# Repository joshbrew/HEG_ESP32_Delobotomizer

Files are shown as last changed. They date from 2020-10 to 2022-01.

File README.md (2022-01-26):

# HEG ESP32 - Delobotomizer Edition

Official repository for the HEGduino V2 Delobotomizer firmware, software, and designs.

### [WebApp: Brains@Play](https://app.brainsatplay.com)
- This will replace the original software and is MUCH more robust, we are still doing a lot of legwork to get all of the quality of life features we want into it but welcome to the new multi-bci community framework for the web! 
- Chrome only for desktop, works on Android and in VR. 
- Find the install button via the settings button in the top right of the browser.
### [Getting Started (click me)](https://github.com/moothyknight/HEG_ESP32_Delobotomizer/blob/main/Guides/GettingStarted.md)
### [Updating Your Device](https://github.com/moothyknight/HEG_ESP32_Delobotomizer/blob/main/Guides/Updating.md)
### [Whitepaper](https://github.com/moothyknight/HEG_ESP32_Delobotomizer/blob/main/Guides/Open%20Source%20HEG_FNIRS%20Whitepaper.pdf)
### [Old Progressive Web App (no longer updated)](https://hegalomania.netlify.app) 
- Original webapp demo, use via Chrome for Serial USB support. Use BLE mode if the USB device is not recognized in browser, this is a known issue. If that fails use the web server with the device in WiFi mode.

### If your browser won't identify the USB connection, try installing the VCP for Windows (or Mac) drivers here: https://www.silabs.com/developers/usb-to-uart-bridge-vcp-drivers

## Firmware

The Firmware folder contains a .bin file that you can use via the on-board web interface to update the device. There are Arduino libraries and firmware code files for custom code, you will need the ESP32 module additionally for Arduino.

Simply connect to the wifi network named "My_HEG" when the device is powered up with password "12345678"

In your preferred browser, enter "192.168.4.1" into the address bar. You should see an interface show up. Click on the Update button to go to the update page.

Now follow the instructions on screen to browse for the .bin folder that you may download from this repo. Wait for it to finish uploading then reconnect to the HEG after that's taken care of if it does not do it automatically. Voila!

## Progressive Web App (WIP): https://hegalomania.netlify.app

Our new preferred method for using the HEG, a state of the art Progressive Web App! 

Open this link to use your HEG in a Chrome browser or Android for instant access to using your device. This is being updated to a React app with a more familiar UI and a more concise code base to expand from.

You may install it locally on desktop or mobile as well just like any app and create desktop shortcuts. For desktop open the settings bar in Chrome and click "Install HEG Alpha." The USB mode only works in chrome right now as it is a development feature. You can enable this feature by going to chrome://flags and enabling the "Experimental Web Platform features" flag. For mobile it should prompt you to install, if not find the install button in your chrome settings menu on mobile.

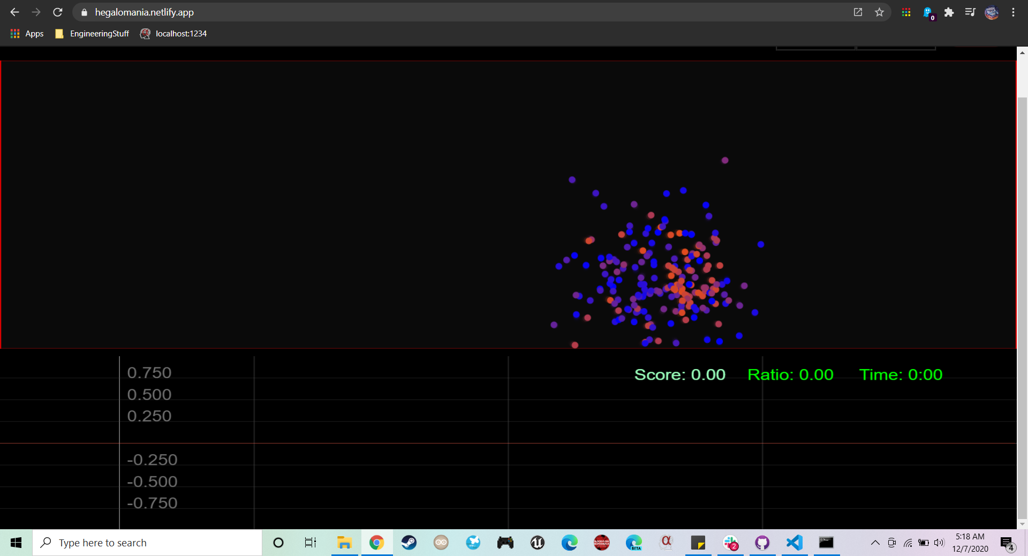
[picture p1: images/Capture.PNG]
Boids


## Boot routine

The newer firmware contains a new boot-up routine for making it easier to identify streaming modes on the device. It will flash when powered up to indicate which mode it's in.

On boot:
* Two fast blinks: BLE mode
* Three fast blinks: WIFI mode
* Four fast blinks: Bluetooth Classic (Serial) mode

The button on the newer devices puts your device to sleep. There will be a switch added next to control device settings.

Since your device is covered in tape this will help you find the reset button if I didn't mark it for you:
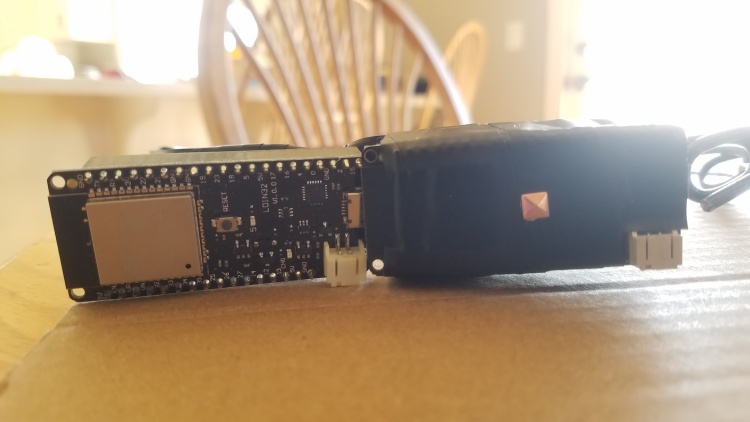
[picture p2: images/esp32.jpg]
esp32


## Device Commands (accessible via app (Send Command button) or serial monitor)

* 't' - Turn sensor ON (automatic)
* 'f' - Turn sensor OFF, device will go to sleep after 10min of inactivity
* 'b' - BLE mode toggle. Toggles back to WiFi mode.
* 'B' - Bluetooth Serial toggle. Toggles back to WiFi mode.
* 'W' - Reset WiFi credentials (if it won't connect to your router)
* 'R' - Reboot device
* 'S' - Enter deep sleep mode e.g. to save battery
* 'u' - USB only output mode (no wireless signals)
* 'o' - Fast output mode (<20 byte packets for Android Web BLE)
* 'L' - External LED mode, configured for pins 12 and 14 to run LEDs and be sampled.
* 'N' - Toggle SPO2 output (experimental, not working properly yet)
* 'D' - Toggle Debug output (for using Arduino's graphing)
* 'e' - Toggle exposure settings: slow, fast, and default. default has the slowest output rate but samples faster than slow mode with more averaging.
* 'l' - Toggle LED protocols in this order: Ambient,IR,2 IR (AMBIENT, LED2, LED1+2); Red,IR,2 IR (LED3, LED2, LED1+2), Red = IR (LED1, LED2, AMB), or Default (LED3,LED2,AMBIENT)
* 'X' - DC filter toggle
* 'F' - Digital filter toggle
Note, use the first setting with the command 'l' if your red LED is underperforming. This will make the software compare Ambient and IR, and optional both IR LEDs for extra strength. For some reason the red output is not as consistent for some people.

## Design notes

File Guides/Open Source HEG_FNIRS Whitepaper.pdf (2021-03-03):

Joshua Brewster
October 2020

## Open Source, Low Cost, Scalable fNIRS/HEG Whitepaper

Contents

Abstract | 2
Acronyms | 2
FNIRS Overview | 3
HEG Biofeedback Overview | 9
List of HEG Case Studies | 17
HEG Alpha | 18
Citations from Hyperlinks | 24

Abstract:
This whitepaper is to cover what I’ve learned from functional Near Infrared Spectroscopy (fNIRS) and Hemoencephalography (HEG) biofeedback as well as my development progress on open source low cost tools for anyone to jump into this space and benefit from it either for education or home therapy. These are important emerging imaging and therapeutic technologies as they offer a low cost and low abstraction method to work with live or recorded information from the brain. This is paired with a type of brain blood flow training for biofeedback therapy that allows users to increase their baseline brain perfusion in their prefrontal cortex and beyond. This field promises even more interesting monitoring methods and psychiatric tools akin to functional Magnetic Resonance Imaging (fMRI) with the use of tomography (DOT), laser interferometry (OCT), and deep learning feature decoders to understand brain activity. Our goal is to carve a path for open source efforts in this area by developing low cost tools and free software through reproducing different public domain hardware and experiments. We are sharing working and tested plans free, and hardware low cost.

Acronyms:
fNIRS - Functional Near Infrared Spectroscopy HEG - Hemoencephalography
EEG - Electroencephalography
HbO2 - Oxygenated Hemoglobin
Hb - Deoxygenated Hemoglobin SpO2 - Pulsatile Oxygen Saturation
CBF - Cerebral Blood Flow
DOT - Diffuse Optical Tomography
fMRI - Functional Magnetic Resonance Imaging OCT - Optical Coherence Tomography

fNIRS overview:

Here will give a brief overview of the essential concepts of Functional Near Infrared Spectroscopy (fNIRS) and brain blood flow biofeedback. The Hemoencephalography (HEG) device is simply a single sensor fNIRS device with red and infrared wavelengths standard to pulse oximetry, and 3 cm spacing for depth readings. Alternatively it has been done with thermocouples to just measure IR radiation off your forehead, while photodiodes also include optical wavelengths. You can view the original patent 5995857 by Hershel Toomim and Bob Marsh, now public domain, online. (https://patents.google.com/patent/US5995857A/en)

fNIRS is the application of near infrared light, and more generally optical wavelengths, for the purpose of imaging the surface of the brain and monitoring Cerebral Blood Flow (CBF). It is much cheaper but not as complete as a functional Magnetic Resonance Imaging (fMRI) scan with tracer injections, though it can still elucidate a ton of useful structural and functional data about the brain. The skull is highly translucent and even lends itself well for optical imaging of the brain. This is accomplished by placing LED or laser emitters with specific wavelengths at specific distances from photosensors on the scalp or forehead and flashing them repeatedly while reading the response on the photodiode. Your pulse for example is plainly visible by this method and blood oxygen can be calculated.

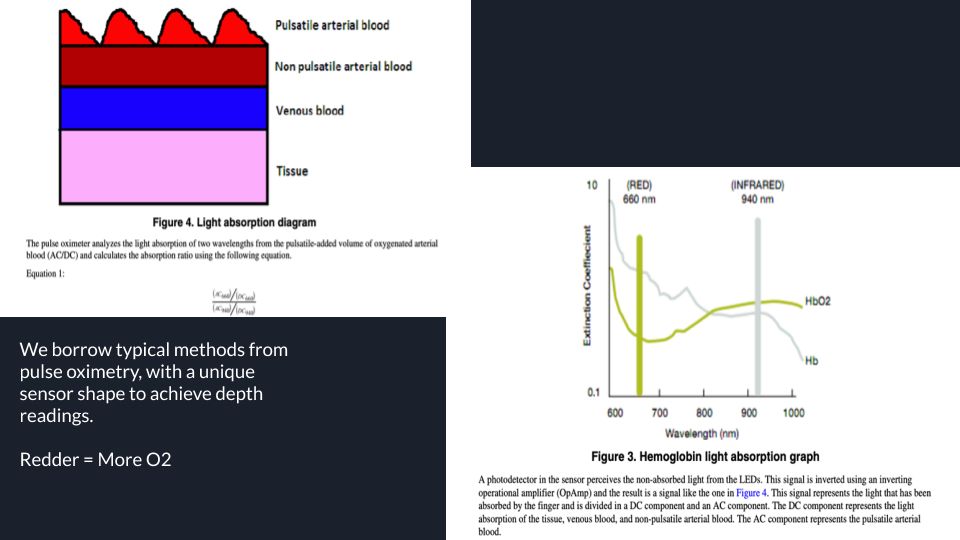
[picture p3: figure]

Optical wavelengths between Green - usually Red or Far Red - and Near-Infrared are generally chosen, one above 810nm and one below as Hb and HbO2 have opposing absorption indexes above and below that point, and are identical at that point. This creates a relationship that can be used to empirically calculate oxygen saturation and monitor blood flow. Pulse oximeters are probably the most universal application of fNIRS used for skin surface or fingertip pulse and pulsatile oxygen (SpO2) measurement.

This goes much further, however, as some optical wavelengths have deeper penetration than others, peaking apparently at 1064nm (https://www.spiedigitallibrary.org/journals/journal-of-biomedical-optics/volume-25/issue-09/097003/Diffuse-correlation-spectroscopy-measurements-of-blood-flow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) in the Near-Infrared spectrum. Photodiode and emitter pairs can even be densely arrayed to enable image reconstruction, and the curvature of the skull allows estimation of light paths between source and sensor pairs to perform 2D or 3D reconstruction using techniques similarly seen in geological surveying or electrical tomography. With mapping techniques especially demonstrated by a little-known piece of tech called Diffuse Optical Tomography (DOT), we can begin to functionally image the brain and spatially monitor metabolic and blood flow activity.

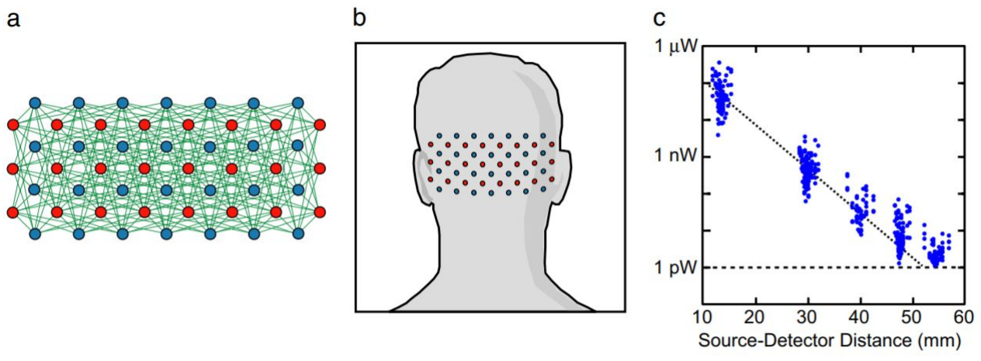
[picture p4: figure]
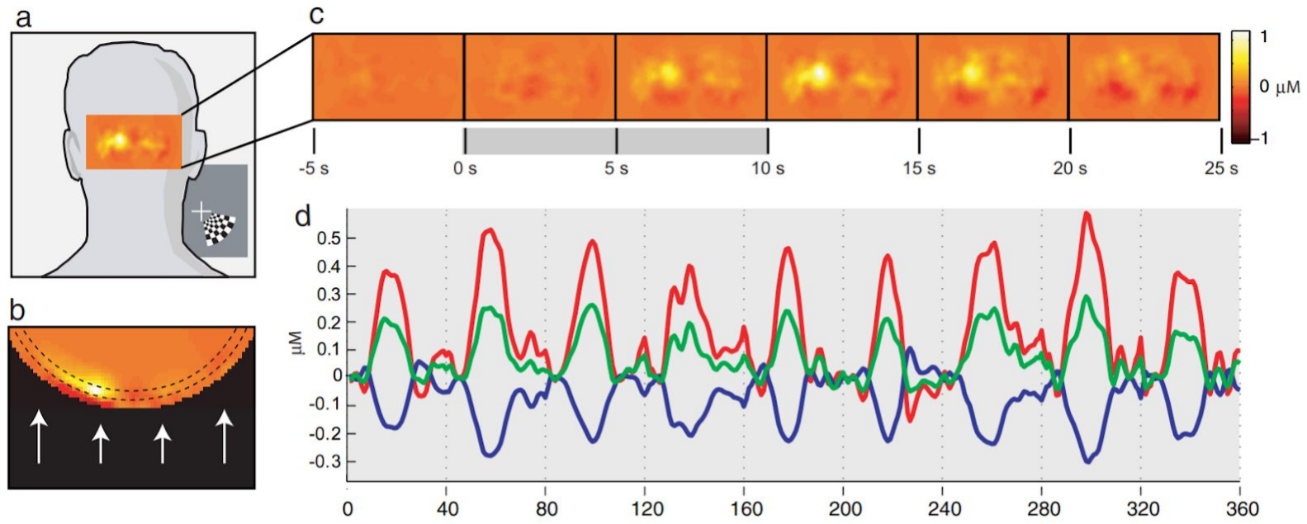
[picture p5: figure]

Source: Retinotopic mapping of adult human visual cortex with high-density dif use optical tomography (https://www.pnas.org/content/104/29/12169)
- Ben Zef , Brian White, Hamid Deghani, Bradley Schlagger, Joseph Culver (2007)

In the above image you can clearly see the two hemispheres of the visual cortex activating using only 28 sensors and 24 emitter pairs in the near-infrared range. My favorite study involving fMRI data made deep learning-assisted reconstructions of images and videos from visual cortex activation patterns as seen in the next image, which ideally can be accomplished using fNIRS. In the next image you can see how deep learning of fMRI activity gets vaguely close to what the person was looking at, and that’s spooky enough. There are other impressive studies (https://news.berkeley.edu/2011/09/22/brain-movies/) out there involving similar data for doing video reconstruction from the visual cortex.

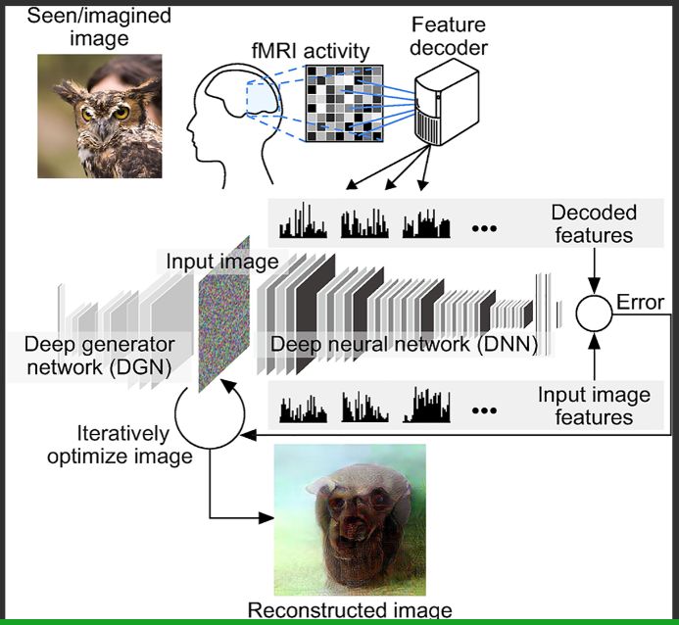
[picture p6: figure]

Source: Deep image reconstruction from human brain activity (https://journals.plos.org/ploscompbiol/article?id=10.1371/journal.pcbi.1006633) - Guohua Shen, Tomoyasu Horikawa, Kei Majima, Yukiyasu Kamitani (2017)

This deep image reconstruction technique gets more interesting the more you look:

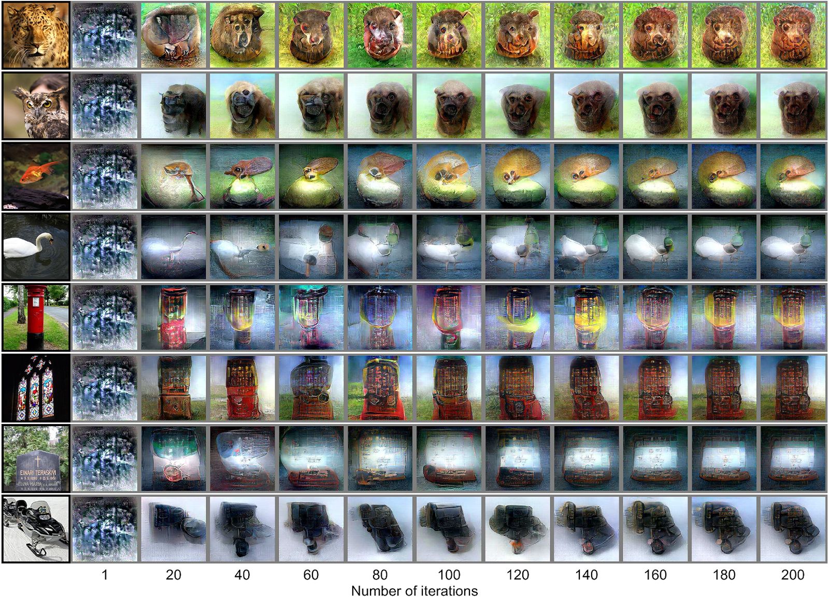
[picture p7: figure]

Source: Deep image reconstruction from human brain activity (https://journals.plos.org/ploscompbiol/article?id=10.1371/journal.pcbi.1006633) - Guohua Shen, Tomoyasu Horikawa, Kei Majima, Yukiyasu Kamitani (2017)

Even rough information can lead to fairly accurate categorizations by deep learning networks, which are picking signal out of noise and comparing it to a learned image database. What is striking to me, when paying special attention to the church window reconstruction in the above image, is that the visual cortex may also blend that image with categorical archetypes encoded within the visual cortex. The church window gets painted onto an obelisk in a grassy field from the looks of it, and to me that suggests Jungian-like object archetypes existing within our sensory processing field when chunking visual input or any sensory input for that matter, likely for efficiency. It’s a weird but not an original idea. This can be related to a recent publication (https://github.com/poloclub/cnn-explainer) looking at how convolutional neural networks (CNNs) encode different categories into its neurons by visualizing what those neuron ensembles actually encoded - where CNNs are heavily based off of the structure of the human visual cortex:

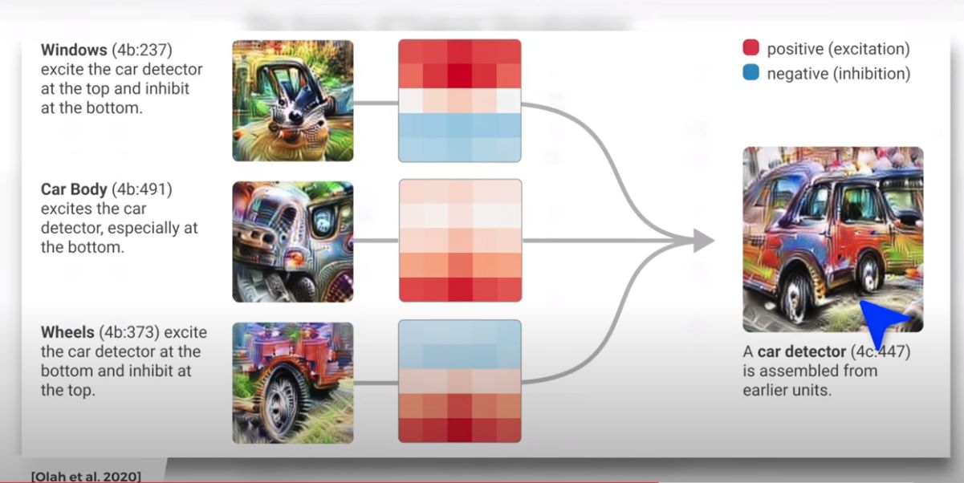
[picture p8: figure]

Source: CNN Explainer: Learning Convolutional Neural Networks with Interactive Visualization. (https://arxiv.org/abs/2004.15004) Wang, Zijie J., Robert Turko, Omar Shaikh, Haekyu Park, Nilaksh Das, Fred Hohman, Minsuk Kahng, and Duen Horng Chau. (2020)

You can see how the different parts of the car get encoded as amalgams of different labeled feature sets that look like trippy fractal meta images, representing all of the different images exposed to the neural network during training. This all suggests a powerful imaging tool for gaining some much deeper insights into human visuospatial psychology and more by live decoding the brain’s actual activity, though that’s pretty far out, dude. Using machine learning decoding comes with a lot of potential confirmation bias problems, too.

“What we call ‘reality,’ consists of an elaborate papier-mâché construction of imagination and theory filled in between a few iron posts of observation.” - Donald Hoffman (https://www.youtube.com/watch?v=3MvGGjcTEpQ) in The Case Against Reality: Why Evolution Hid the Truth from our Eyes

This is just what’s possible with diffuse optical imaging or Fast Optical Signal (https://www.ncbi.nlm.nih.gov/books/NBK20223/) spatial mapping by another name, and uses a lot of mathemagic to make it happen. It is also constrained by the speed of your processing and LED routines, and sensor array density. A commercial example of this is the NIRSIT device for frontal lobe monitoring with around 200 overlapping sensors on the forehead. So what about modern laser scanning tech? This leads to even more interesting but much more difficult infrared imaging featuring interferometry. This is best demonstrated using Optical Coherence

Tomography (OCT), where you apply the similar fNIRS principles to microscopy and get freaky with mirrors, beam splitters. and interferograms.

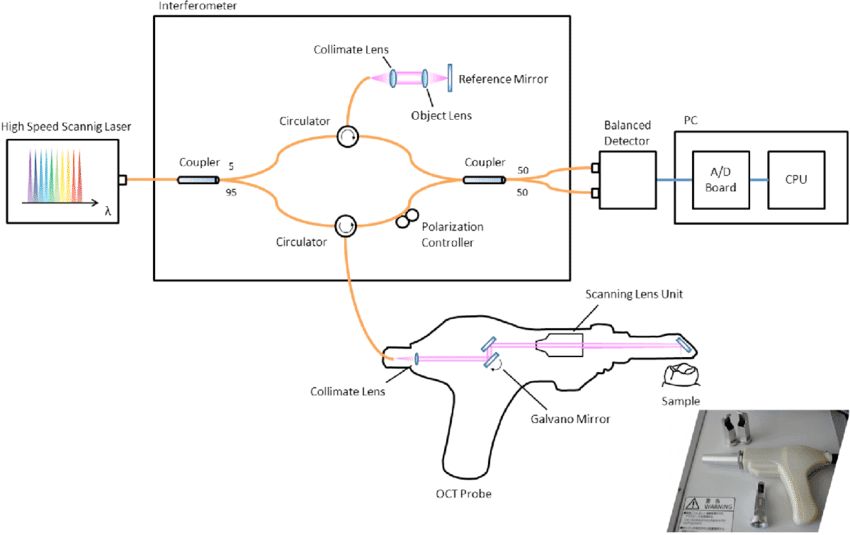
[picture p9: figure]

Source: Assessment of natural enamel lesions with optical coherence tomography in comparison with microfocus X-ray computed tomography (https://pubmed.ncbi.nlm.nih.gov/26158079/) - Espigaras et. al. (2015)

OCT provides another level of optical imaging and is currently only used for microscopic applications, requiring very high coherence lasers and lenses and other expensive optical equipment. This is able to perform miracles like high res 3D fingerprint detection or 3D angiography to image dense capillary networks, and more. A couple main applications are in eye clinics to look for issues in your cornea layers or experimentally in high security zones for extra fingerprint verification.

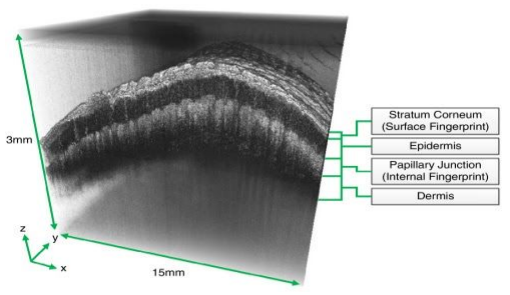
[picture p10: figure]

Source: Automated spoof-detection for fingerprints using optical coherence tomography (https://www.researchgate.net/publication/301745082_Automated_spoof-detection_for_fingerprints_using_optical_coherence_tomography) - Luke Nicholas Darlow, Leandra Webb, Natasha Botha (2016)

And who said modern science isn’t cool enough? This of course comes on the heels of massively improved manufacturing techniques and computer technology which can handle the high resolution and high processing speeds required for this 3D microscopy. What if you can scale this up, however, to effectively create a much higher resolution DOT image that is halfway in-between the high resolution microscopy and the rough 28 sensor DOT image (which still highlights brain hemispheres and some gyrations as seen above)? This has many engineering challenges associated, but it probably can be done. This would improve resolution especially at deeper layers, and can be enhanced even further with the use of dynamic focus (https://pubmed.ncbi.nlm.nih.gov/26662065/) and more tricks from RF and astronomy.

HEG Biofeedback Overview

First, familiarize yourself with various Cerebral Blood Flow (CBF) studies in this informal list, which demonstrate how different physical and psychological stresses, not to mention aging, have significant impacts on CBF. This helps stage an argument for why therapies targeting this process may be so significant to improving overall wellbeing:

Perfusion MRI to study CBF under psychological stress - Wang et. al. https://www.pnas.org/content/102/49/17804.short

Cerebral Blood Flow changes in socially phobic people during stressful speaking tasks - Tillfors et. al. https://ajp.psychiatryonline.org/doi/full/10.1176/appi.ajp.158.8.1220

CBF changes in cops with PTSD - Lindauer et. al. https://www.sciencedirect.com/science/article/abs/pii/S0006322304008546

Cerebral Hypoperfusion in migraine patients - Woods et. al. https://www.nejm.org/doi/full/10.1056/NEJM199412223312505

Cerebral Hypoperfusion and the onset of dementia - Ruitenberg et. al. https://onlinelibrary.wiley.com/doi/abs/10.1002/ana.20493

Cerebral Hypoperfusion in children with dysphasia and ADD - Lou et. al. https://jamanetwork.com/journals/jamaneurology/article-abstract/583298

Cerebral Hypoperfusion accelerates Alzheimer's - Okamoto et. al. https://link.springer.com/article/10.1007/s00401-011-0925-9

Effects of Aging on Cerebral Blood Flow - Ances et. al. https://onlinelibrary.wiley.com/doi/full/10.1002/hbm.20574

Sympathetic nervous system effects on CBF - Seifert et. al. https://www.ncbi.nlm.nih.gov/pubmed/21963551

Cognitive training to improve resting Cerebral Blood Flow in the PFC in adults - Mozolic et. al. https://www.frontiersin.org/articles/10.3389/neuro.09.016.2010/full

Exercise increases CBF, NIRS study - Ide and Secher https://www.sciencedirect.com/science/article/pii/S030100829900057X

CBF changes with volitional breathing - Colebatch et. al. https://physoc.onlinelibrary.wiley.com/doi/abs/10.1113/jphysiol.1991.sp018824

Tasty-looking food increases cerebral blood flow - Koyama et. al. https://www.tandfonline.com/doi/abs/10.3109/09637486.2015.1118618

What makes the HEG device special and rather unorthodox is that it’s a purposefully stripped down tool meant to capture general rises and falls in blood oxygen and the corresponding metabolic action in the targeted area of your brain. Breathing patterns for example are fairly clear, as well as when the user is paying attention or stressed out. These are all clearly marked by slow or even rapid changes in blood oxygen content in the prefrontal cortex. Increased activity corresponds with increased regional CBF when neurons draw on capillaries to meet their energy demands to fire. Compared to EEG the results are immediately apparent without any complex information processing required and happens slowly enough to be quite visible to the naked eye. This allows users to perform a type of brain exercise by breathing and paying attention to their thought patterns and seeing how prefrontal cortex oxygen saturation changes. Remember this is the same tech used for that cool imaging in the last section, just totally stripped down to remove any abstraction.

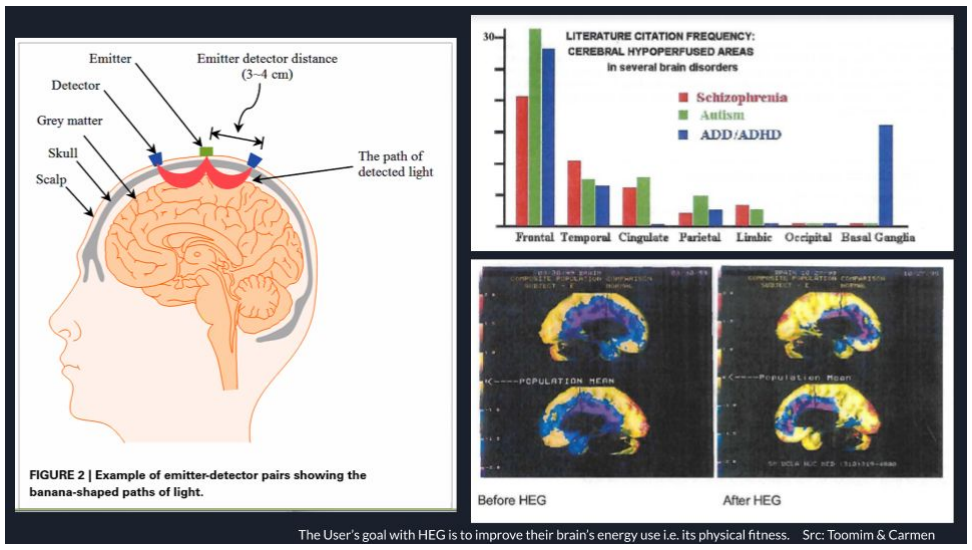
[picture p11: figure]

The Biofeedback Institute of LA had a few hundred SPECT scans performed on dozens of patients over several month periods while training with their HEG device several times per week. BILA noted how often issues like hypofrontality, i.e. reduced frontal lobe metabolism, show up in so many studies of mental disorders, and this therapy offered a direct remediation method quite unique to this technology. They recorded and reported fairly dramatic increases in average perfusion in the brain by population mean (see bottom right in the image above) after several months of HEG training.

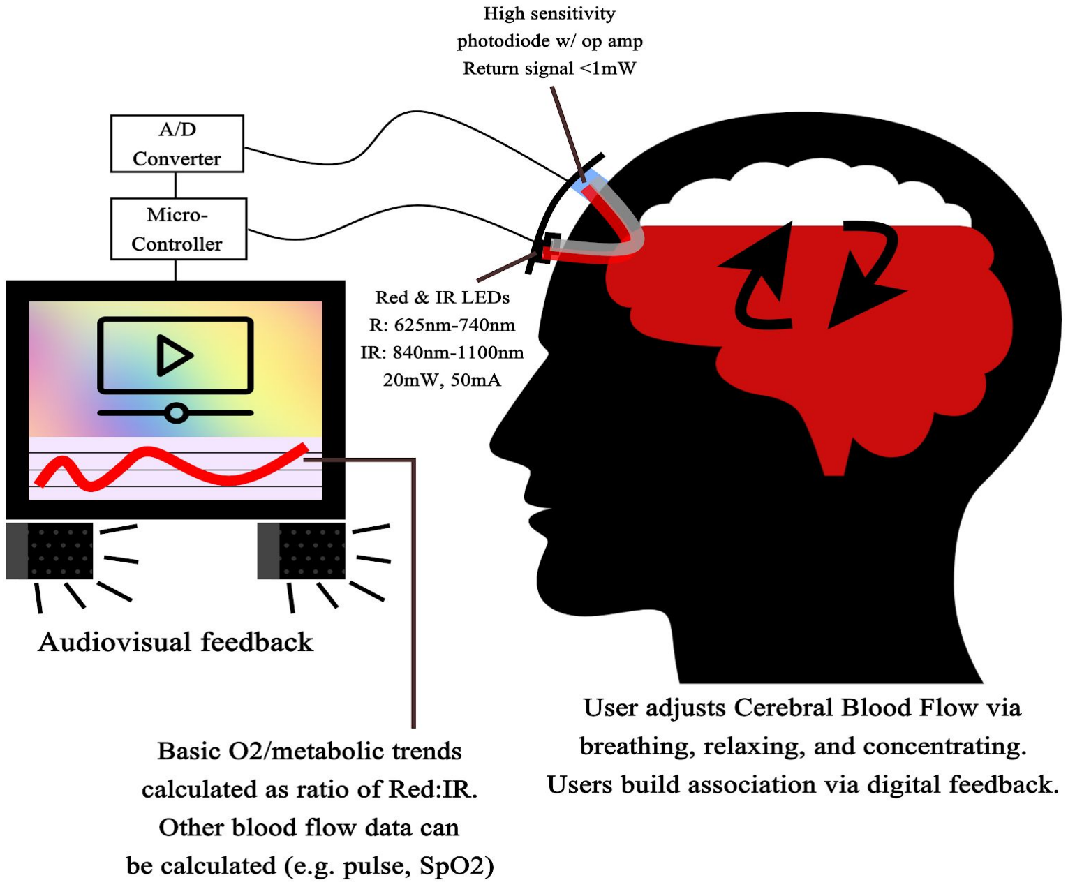
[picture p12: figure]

To begin to explain the breathing exercise’s effects, we need to talk about volitional breathing. Volitional breathing, i.e. controlled breathing, is a time-tested tactic to redirect oneself in the moment as well as strengthen one’s overall sense of clarity and presence. It’s obvious that optimal breathing patterns will enable better oxygen delivery and therefore bodily functioning, and different breathing styles can stress or relax the body in interesting ways as practiced by a lot of yogis or notably by Wim Hof. (https://en.wikipedia.org/wiki/Wim_Hof) Oh but there’s more to this story.

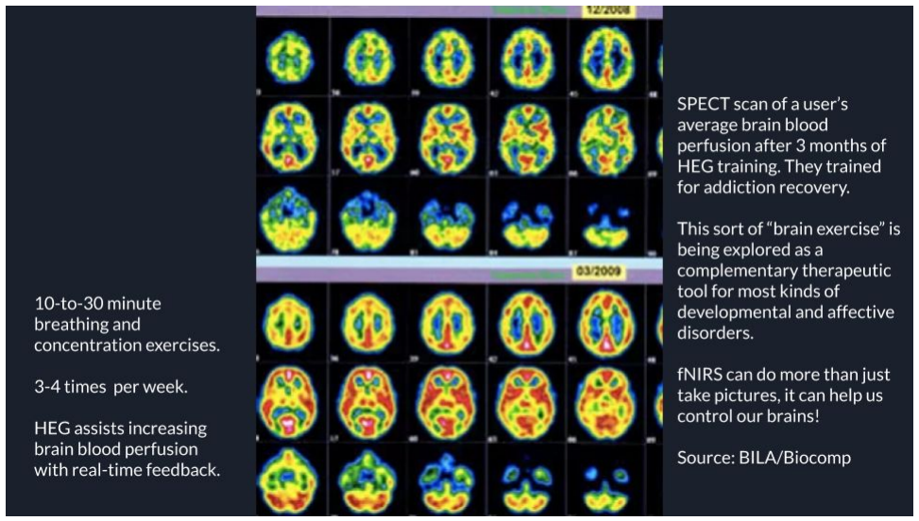
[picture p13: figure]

A 2018 study (https://journals.physiology.org/doi/full/10.1152/jn.00551.2017) with implantable EEG in a seizure patient found that the anterior cingulate cortex (ACC) would oscillate in correspondence with controlled breathing patterns then stop cohering nearly as much when automatically breathing. This shows that the ACC among many others is quite involved when controlling and paying attention to our breath, and this networks with the rest of our frontal lobe as well as plays important roles in regulating the limbic system - notably the amygdala. A 2018 mouse brain study (https://www.nature.com/articles/s41467-018-05090-y) in Nature magazine discovered that stimulating the ACC reduced instinctual fear responses due to its direct connection to the amygdala and other related areas for fear (same with the olfactory bulb). (https://www.nature.com/articles/s41467-018-03988-1) Lack of activity in the ACC conversely increased instinctual fear response. This helps demonstrate how the frontal cortex plays a role in inhibiting instinctive reactions, which is a well known idea. However, this corresponds with regions of the brain that we now know we have direct influence on via controlled breathing, with several other networks probed in the volitional breathing study also correlating to either controlling breathing and/or being aware of breathing.

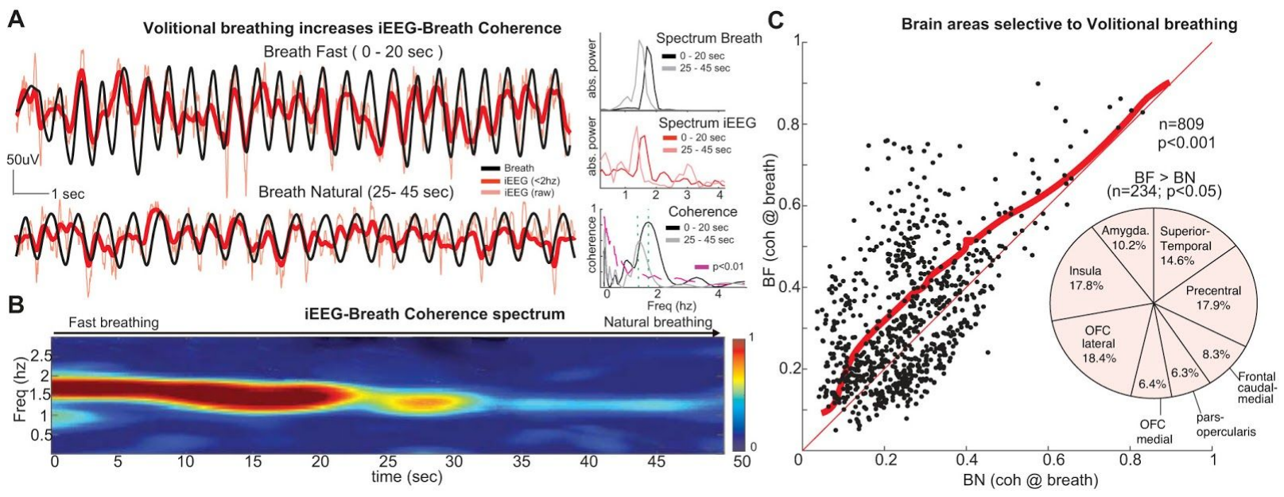
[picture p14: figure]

Source: Breathing above the brainstem: volitional control and attentional modulation in humans (https://journals.physiology.org/doi/full/10.1152/jn.00551.2017) - Jose Herrero, Simon Khuvis, Erin Yeagle, Moran Cerf, Ashesh Mehta (2018)

Now let’s talk about energy use for a minute and how stimulating the neocortex enables healthier cortical growth. This may help us understand why a direct brain stimulation method via controlled breathing may be so significant and help explain why it’s been such a long held practice. This is also how we can begin to establish the idea of “brain exercise” as a real thing and something with a lot of nuance and potential benefits along with technologically-assisted psychotherapy.

The brain directs energy where it needs. It’s like a water balloon with limited blood supply and it’s squeezing itself in different places to direct that blood supply to the most-needed areas so that they can operate, recover, and self-clean. Your brain also eats at least a steady 20% of the body’s resting state (https://www.ncbi.nlm.nih.gov/pmc/articles/PMC124895/)

calories (https://www.ncbi.nlm.nih.gov/pmc/articles/PMC124895/) or about 300 calories/day - making it the most high demand organ in your body when compared to body mass. Young children’s brains have been hypothesized to burn as high as 2/3rds (https://www.pnas.org/content/116/27/13266) of the body’s energy with all of the major growth the brain undergoes, making it that much more sensitive to changes in the developmental environment.

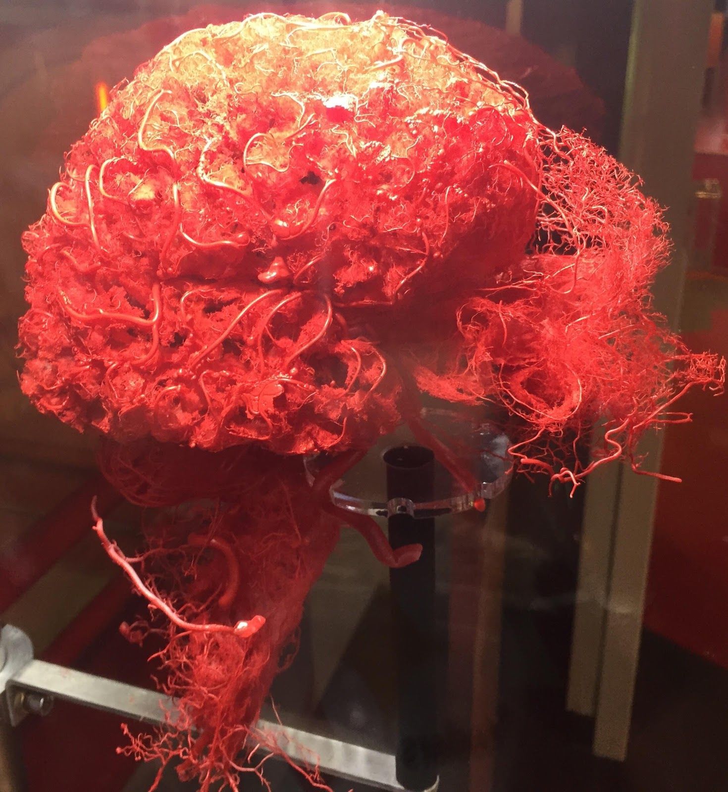
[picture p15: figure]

Human brain vascular system. Source: Carnegie Science Center in Pennsylvania

High demand means high vascularization (https://www.ncbi.nlm.nih.gov/pmc/articles/PMC4678116/) i.e. density of blood flow networks - a process managed by our glial and endothelial cells. Without that process, brain cells can’t grow, heal, or fire on demand, while the demand also encourages more vascularization by signaling capillaries to grow into the networks as part of the reinforcement process. Astrocytes (https://www.ncbi.nlm.nih.gov/pmc/articles/PMC6562853/) - which make metabolites and neurotransmitters for neurons, manage hundreds of thousands of synaptic clefts each, and help perform vasodilation - can be stimulated (https://www.nature.com/articles/s41467-019-13956-y) with diaphragmatic breathing (http://projects.hsl.wisc.edu/SERVICE/modules/12/M12_CT_ThePowerOfBreathDiaphragmaticBreathing.pdf) (a tried and true stress and anxiety relief technique) to regulate regional blood supply like a baroreceptor, and are another fundamental yet underrepresented (https://www.ncbi.nlm.nih.gov/pmc/articles/PMC6379461/) part of the brain’s processing. Exercise and stimulation also induces astrocyte plasticity (https://www.ncbi.nlm.nih.gov/pmc/articles/PMC4914586/) along with neuroplasticity (https://www.ncbi.nlm.nih.gov/pmc/articles/PMC6296269/) and angiogenesis (https://www.ncbi.nlm.nih.gov/pmc/articles/PMC5577549/) to meet the new demands on the neurons as they form new connections and modify old ones. It all happens all at once as a complex system, and the non-neuronal cell structures might still be doing much more to contribute to consciousness and memory beyond maintaining homeostasis. What we can take away, however, is that we have the full ability to influence this whole system through exercise, especially with our breath.

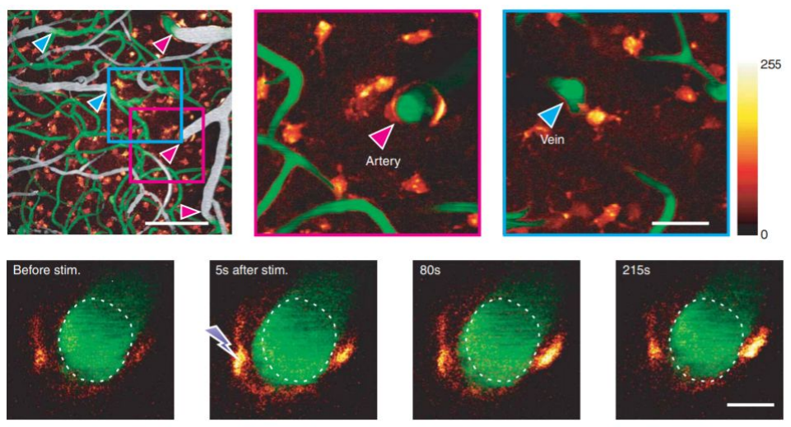
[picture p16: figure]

Astrocytes stimulated (orange) to induce arterial vasodilation (green). Source: Astrocyte-mediated control of cerebral blood flow (http://www.cns.nyu.edu/events/spf/SPF_papers/takano_etal_2006.pdf) - Takano et. al. (2006)

These different cellular phenomena in the brain demonstrate a clear and verifiable precedent for how breathing and increasing blood flow via exercise can have real structural and functional changes in many key areas of the brain, related to all kinds of mental processes and psychiatric issues. It shows how intense the cellular processes really are for just building the infrastructure that supports your biological neural network, and how it must adapt at every step of the way to keep up with your learning and living.

Breathing exercise specifically has several well-mapped and interesting relationships to mental processing via breathing’s specific coupling with many different important brain systems. This is likely due to its big role in keeping us alive, sensing, and communicating. It’s just like how all of the other functions we perform are now being found to have specific networks in our brain, and we can stimulate those networks to grow and reinforce by performing and practicing those functions along with practicing good health. This also offers a way to interact with and remediate many of the involuntary CBF changes cited in the studies at the beginning of this section and in countless others not highlighted. The brain is like a muscle in that sense, and must “fire together to wire together.” This exercise can also increase uptake of different types of learning and memorization as a priming method.

With this all in mind, what I suggest is simply that we have a very interesting and universal way to better understand and reinforce many systems in our brain. It offers the opportunity to reinforce our mind-body connection very pragmatically, and just with simple controlled breathing exercises. It’s nothing new, but I am attempting to link it with clinical evidence down to the cellular level so there is much less doubt about this reality and more dignity for its practitioners. However, with a clearer holistic model developed as more related physiological studies come out, we ought to be able to use this as a kind of old-school but valid deep brain stimulation. (https://www.ncbi.nlm.nih.gov/pmc/articles/PMC3969941/) We can likely learn to very specifically regulate activity in different parts of the brain associated with different mental processes - places otherwise out of reach - with the aid of different breathing techniques to see how functional, morphological, and psychological changes may occur in response. The point is to better understand how we may provide people more relief from mental illnesses and a chance to excel in themselves by more noninvasive, non-pharmacological means so that there are more options and more prevention (of which there are few). This can and should be done with the assistance of low cost monitoring technology like fNIRS for maintaining objectivity as well as introducing new ways to interact with ourselves directly or indirectly.

With regards to the self-interaction allowed by technology, not all of this is conscious and our body is able to interact with much more complex sensory information to inform itself than we may initially realize due to our limited top-down awareness. A great 2015 TED talk (https://www.ted.com/talks/david_eagleman_can_we_create_new_senses_for_humans?language=en) with David Eagleman highlights his contributions on measuring information throughput via vibrations on the skin (https://link.springer.com/article/10.1007/s00221-015-4346-1) (akin to how we read braille). His team found that within days a deaf person could learn to interpret vibrations on a vest, corresponding to audio inputs encoded in specific vibratory patterns, and could interpret spoken words very easily without lip reading. What we can extrapolate from this is that our bodies are processing and encoding much more information and are capable of internalizing all kinds of abstract models for language and self-regulation. This helps indicate that biofeedback - or adding some extra sensors to better indicate our physiological states - has real implications at both the conscious and unconscious levels. Taking this further, our bodies use all of the sensory input it can get to help regulate its internal processing and form new communication pathways to itself and the external world in tandem via reinforcement learning. We are like cybernetic octopuses disguised as apes or something.

Bringing this back down a peg, dozens of case studies over the past two and a half decades indicate repeatable, predictable responses to HEG biofeedback across hundreds of users either considered healthy or with different major symptom profiles like PTSD (https://www.csusb.edu/sites/default/files/upload/file/2016_Reiter%2C%20Andersen%2C%20Carlsson_Neurofeedback%20Treatment%20and%20PTSD_0.pdf) and ADHD. (https://pubmed.ncbi.nlm.nih.gov/29658934/) The next section contains a list of case studies (most of the ones I can find on the internet) and show positive results across the board. I did not have to cherry pick.

List of HEG Case Studies
Here is an informal list of links to many widely varied case studies across many institutions and describe many testable treatment protocols for using the HEG effectively:

Intentional Increase of Cerebral Blood Oxygenation Using Hemoencephalography (HEG): An Efficient Brain Exercise Therapy - Toomim et. al. https://www.tandfonline.com/doi/abs/10.1300/J184v08n03_02?src=recsys

Effects of HEG training at three prefrontal locations - Sherrill https://www.tandfonline.com/doi/abs/10.1300/J184v08n03_05?src=recsys

HEG Neurofeedback Mechanism of Action (ASD focused) - Shoshev https://www.researchgate.net/profile/Mitko_Shoshev/publication/323699457_Hemoencephalography_neurofeedback_-_mechanism_of_action/links/5ab8b34045851515f59f8fc9/Hemoencephalograp hy-neurofeedback-mechanism-of-action.pdf (https://www.researchgate.net/profile/Mitko_Shoshev/publication/323699457_Hemoencephalography_neurofeedback_-_mechanism_of_action/links/5ab8b34045851515f59f8fc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)

Clinical Usefulness of HEG - Serra Sala et. al
https://www.ncbi.nlm.nih.gov/pmc/articles/PMC4869785/

Passive Infrared HEG: 4 years and 100 migraines - Carmen https://www.tandfonline.com/doi/abs/10.1300/J184v08n03_03

HEG Case studies - Toomim and Carmen https://www.brainchanger.co/wp-content/uploads/2018/07/heg_case_studies.pdf

HEG A New Therapy for ADHD: Case Report - Mize https://www.tandfonline.com/doi/abs/10.1300/J184v08n03_06

Evaluation of PFC activation and emotional processing with HEG - Gallart https://www.tandfonline.com/doi/abs/10.1080/10874208.2012.705754

Passive Infrared HEG - Carmen https://www.eeginfo-neurofeedback.se/fileadmin/images/was_ist_neurofeedback/literatur/pIR_HEG_article_10_25_01.pdf (https://www.eeginfo-neurofeedback.se/fileadmin/images/was_ist_neurofeedback/literatur/pIR_HEG_article_10_25_01.pdf)

HEG for Dyslexia - Pecyna
https://link.springer.com/chapter/10.1007/978-94-007-6627-3_26

HEG for Schizophrenia vs Healthy participants - Gomes et. al. https://www.sciencedirect.com/science/article/abs/pii/S0920996417305200

HEG for Migraines without aura - Walker and Lyle http://www.neuroregulation.org/article/view/16213

HEG training for improving brain function with EEG comparisons - Bartosinski et. al. http://82.139.152.144/index.php/pjas/article/download/133/110

HEG training for children with and without ADHD - HEG and QEEG comparisons - Castro et. al. https://www.sciencedirect.com/science/article/abs/pii/S0924933814778095

HEG training with EEG data compared - Sherrill https://www.tandfonline.com/doi/abs/10.1300/J184v08n03_05

### 37 Migraine patients studied with EEG + HEG + Skin temperature - Stokes and Lappin

https://link.springer.com/article/10.1186/1744-9081-6-9

HEG Alpha
So where are we at right now? There are many emerging fNIRS technologies on the market of varying complexity and an even more variable cost, though it is dropping on average like all commercial technologies. I myself have produced a single sensor fNIRS HEG board, first as a cheap off-the-shelf kit and now a more competent and state of the art design using the MAX86141 with a modular and flexible breakout board style. It can be either a foldable fingertip pulse oximeter or fNIRS sensor. These are currently available at https://hegalpha.com as developer kits and come with a simple but functional headband to make it a wearable biofeedback device. The original kit was launched successfully on Crowd Supply and picked up by OpenBCI for their shop. We have sold hundreds without much budget for advertising or flashy designs due to its highly practical purpose.

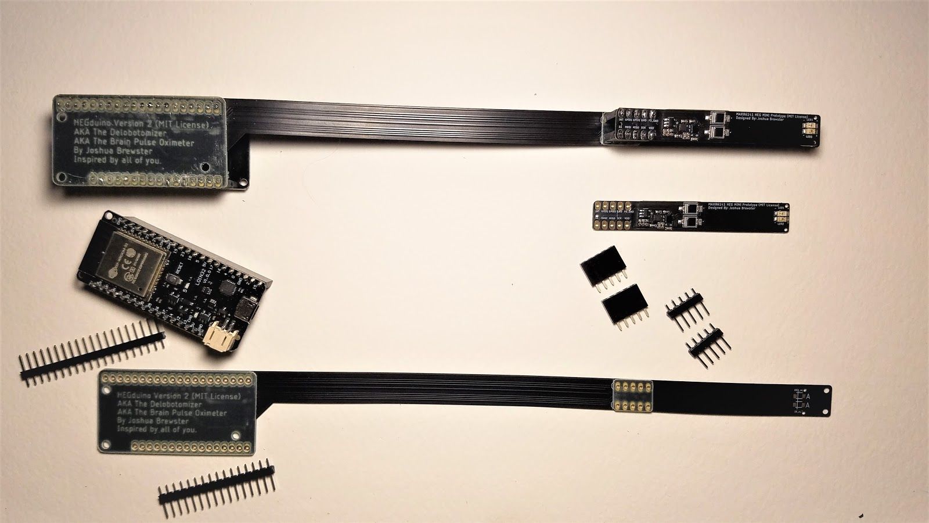
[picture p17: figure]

The Delobotomizer kit features an ESP32 to drive the MAX86141, enabling Bluetooth, WiFi, and Serial USB data transmission and lightweight onboard software via a web server to deliver a robust HTML5 interface. This was developed over the last year and a half with the help of Brain Trainer (from Georgia) and John Chibuk (BlueberryX in Toronto) at certain phases while I helped them prototype their own designs. My own version is available open source under the MIT license or as a purchasable developer kit to support my continuing public domain work.

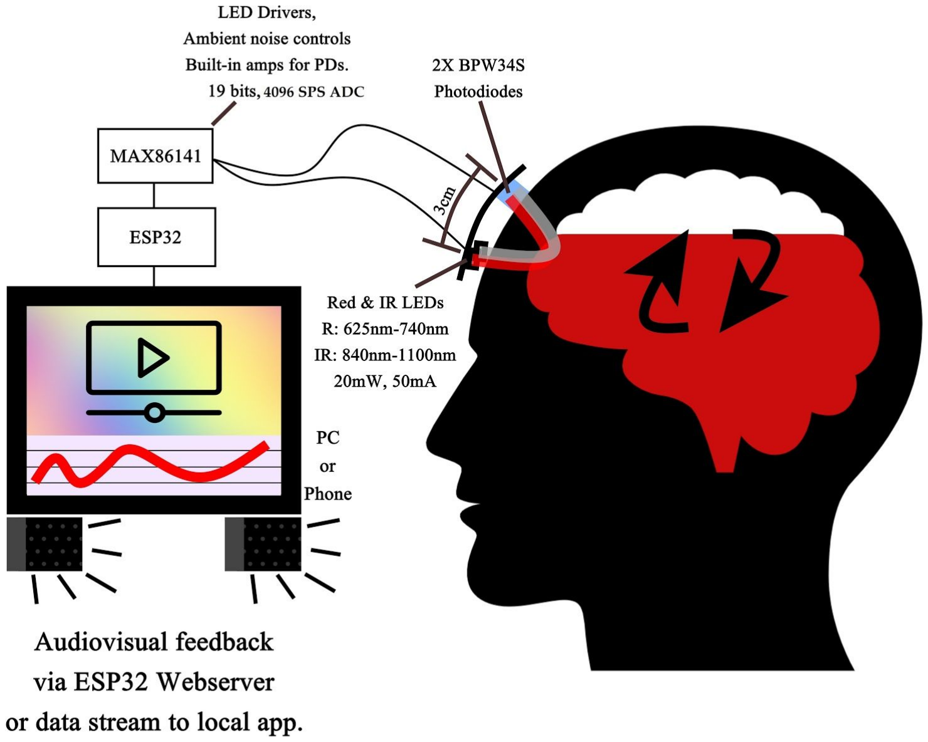
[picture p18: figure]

The MAX86141 is a dual channel 4096sps 19 bit ADC with built in amps and LED drivers to manage photodiodes and up to 6 LEDs. The MAX86141 also has its own automatic data buffering system and some nice hardware noise reduction algorithms to sweeten the deal, all for about $5 in a barely visible BGA package (see if you can spot it above). We used the highest sensitivity photodiodes we could find
- the BPW-34S and bright, fast-pulsing ~650nm and ~950nm LEDs, standard wavelengths for pulse oximetry using common SpO2 algorithms. (https://www.maximintegrated.com/en/design/technical-documents/app-notes/6/6845.html)

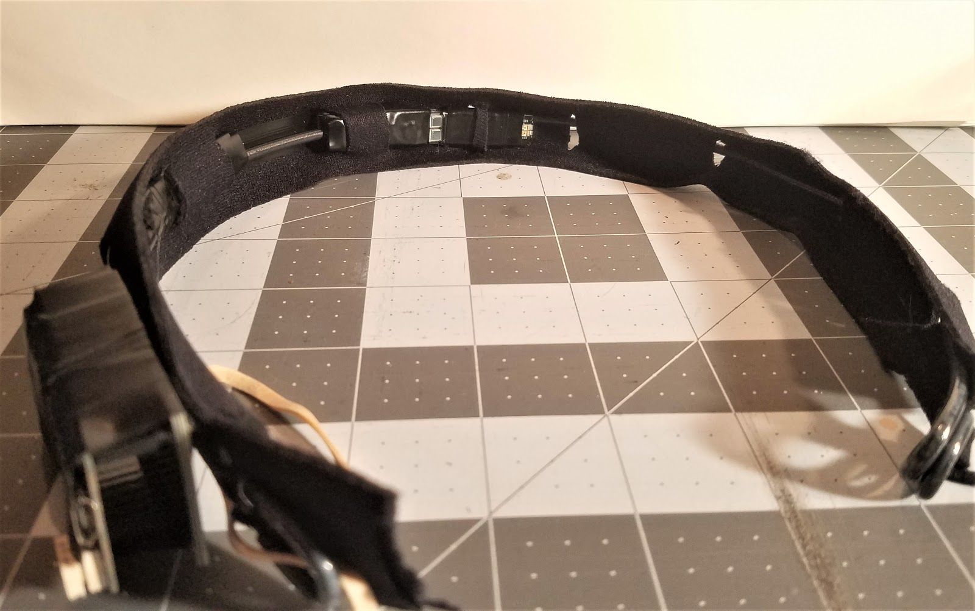
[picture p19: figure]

HEGduino: The Delobotomizer, a homemade wearable dev kit.

Users wear this device on their heads with a simple headset and interact with our streamlined cross-platform javascript software. At the time of writing this exists as either the on-board HTML5 app or a Chrome extension which enables USB or Bluetooth connectivity via virtual COM port.

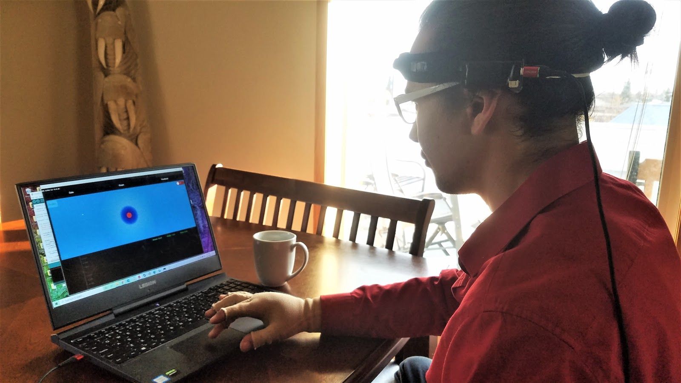
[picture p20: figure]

A user interacting with the software. His brain blood flow creates changes to the different visuals on-screen to help with self-guided biofeedback. Guided exercises and more sophisticated conditioning tools can be developed, while the current visualizations are all passive - which are more ideal for casual sessions.

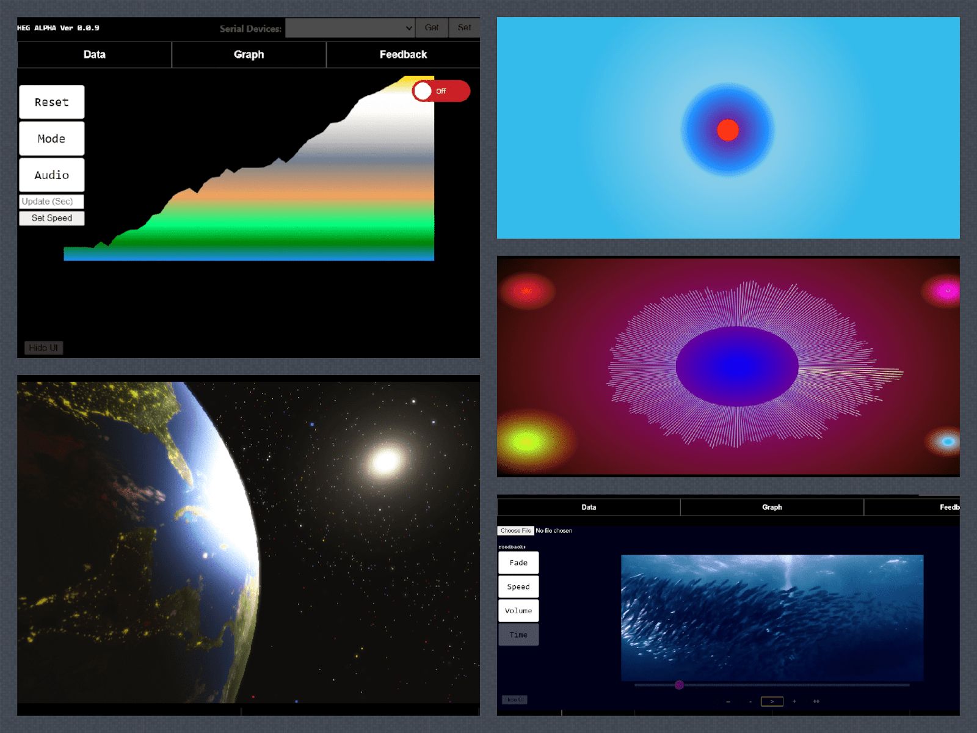
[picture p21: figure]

The interface contains different 2D, 3D, audio, and video feedback options. These are coded entirely modularly via classes with a homogenized format so the API is easy to learn and more features are fairly trivial to plug in or develop on top of. With vanilla HTML5/CSS/JS as the base, it can also be plugged into phone apps or websites to offer robust cross-platform accessibility or remote play. This is now being demonstrated with a Progressive Web App implementation which will provide cross platform access and will be downloadable from a single link on the web.

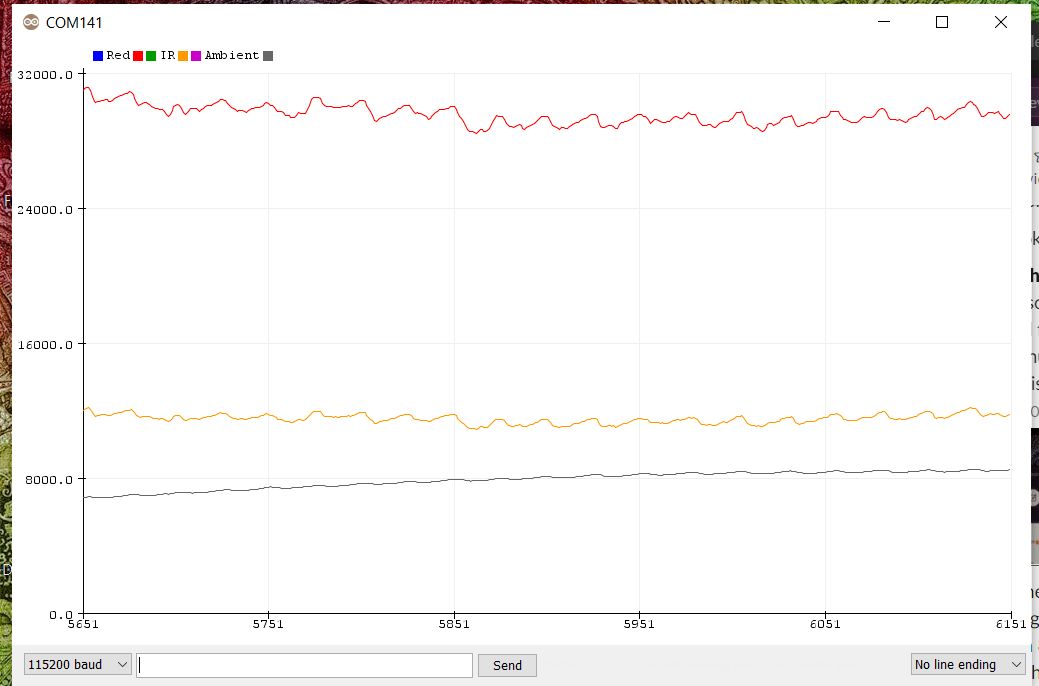
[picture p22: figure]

Data off the forehead with the Delobotomizer (I just like saying it) at 3cm spacing and 29.4us 124mA LED pulses, averaging 32 samples for each pulse at 2048sps. This was not a great controlled test but this was shoving as hard as I could into my scalp to minimize scalp signal. You can see pulse amplitudes even in the ambient light, and even the blood pressure waveforms in the Red and Infrared. While you can see that the Red signal is double the IR, at times it is the other way around depending on location and your physical state. There are rapid, dramatic changes visible even with a 1 sensor signal. This is all done in Arduino since it’s a piece of cake to work with.

The goal with the software was to make the beginnings of an open and relevantly formatted BCI software API and simple game engine (including easy and lightweight plugins like ThreeJS). Each class contains default instantiations of the contained visual features so it’s easier to build a UI and then modify it with CSS. Everything is handled with document fragments for creating highly performant webapps. Web and game engines have also improved dramatically with many standard
communication protocols now on hand to interact with hardware streams, and the ESP32 on the HEG allows a wide variety of ways to connect to different local or remote interfaces. The more generic and reusable we make this API, the easier it is to build a professional feature set in less time on any platform (or all platforms). My goal is to be able to offer comparable software to the professional ones by this method, for free, and make it a robust and performant BCI platform as well as a launchpad for future, better iterations. This is all in a format that is not likely to become obsolete in the near future -rather even more feature-rich with Web 3.0 and the recent addition of great GPU tools like compute shading.

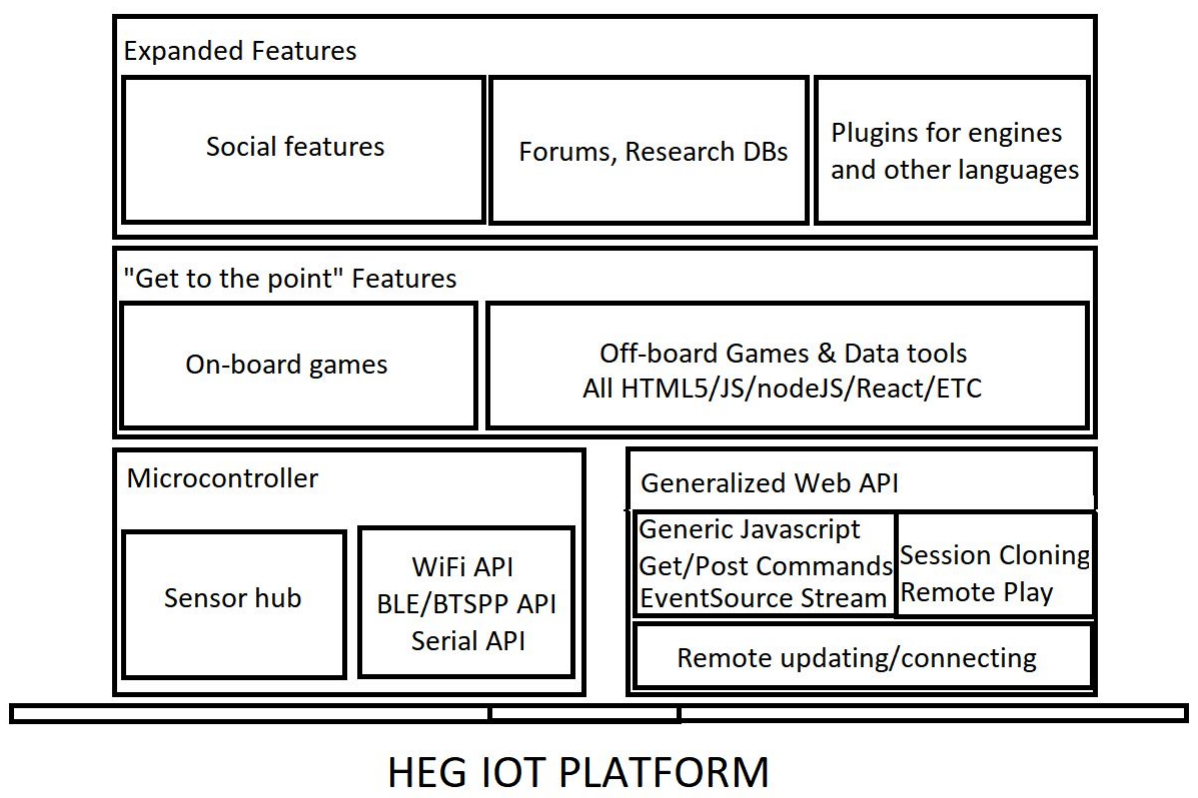
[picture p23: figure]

Here’s a rough idea of the modular software stack. It’s like a RESTful API so nothing gets wasted on the front or backend plus it prioritizes better information throughput and cleaner coding. The idea is to eventually integrate this all into a hosted web server to provide an interesting (but optional) online front end for general home BCI just to improve accessibility and make more use of the online connectivity potential between clients. A native phone application is also planned. You can see demos here: https://hegalomania.netlify.app and here: https://heg-alpha.netlify.app where one is a React port of the interface.

We are informally partnered with the FreeEEG32 project (https://www.crowdsupply.com/neuroidss/freeeeg32) and intend to lump EEG features into our API, and we are developing our own <$50 flexible DOT sensor set (MIT license) (https://github.com/moothyknight/DIY_DOT) to plug into the <$200 FreeEEG32 board (AGPL license). This DOT set mimics the visual cortex fNIRS array back in the fNIRS overview. With the FreeEEG32 as the A/D converter and extra boards tied together as LED drivers for the 24 LED pairs on the device this will be the lowest cost and most enthusiast-friendly DOT headset to date, and the goal is to work up to repeating the image reconstruction study also cited in the fNIRS overview and see if we can begin to parse what our visual cortex is seeing.

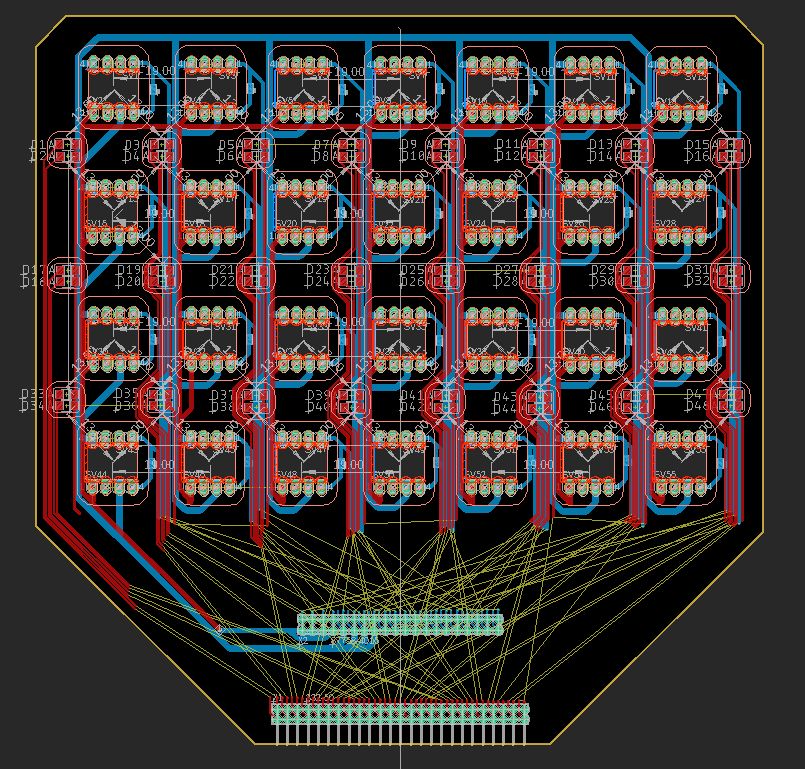
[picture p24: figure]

We are trying to work our way through this weird and wonderful realm of light based sensing and brains. We are developing low cost biofeedback tools and graduating ourselves to imaging, without leaving any stone unturned along the way so that we are continually putting out practical tools for common use and articulating important ideas as best we can. We’re exploring the associated mathematics and doing as much ourselves as possible so we can safely open source it for free and low cost use, as enabling more and more inquiry and collaboration for this fascinating space is a most important goal.

Other interesting open source fNIRS projects to check out:
ninjaNIRS: https://openfnirs.org
OpenNIRS: https://opennirs.org

This will hopefully carry over into a wider coordinated effort with a lot more people involved as we explore new frontiers. Get in touch and let me know your ideas/efforts if you want to collaborate at https://hegalpha.com.

Citations from Hyperlinks
This section is to highlight all of the studies and articles in the embedded links throughout the paper (click on them if you are viewing on a computer). Check all of them out, there are more than 60 links throughout this article, and you haven’t really learned anything if you haven’t looked further beyond my paper as they contain tons of detailed information and images.

Toomim, Marsh. “Biofeedback of human central nervous system activity using radiation detection” USPTO. 1996.
https://patents.google.com/patent/US5995857A/en

Carp et. al. “Diffuse correlation spectroscopy measurements of blood flow using 1064nm light” Journal of Biomedical Optics. 2020. https://www.spiedigitallibrary.org/journals/journal-of-biomedical-optics/volume-25/issue-09/097003/Diffuse-correlation-spectroscopy-measurements-of-blood-flow-using-1064nm-light/10.1117/1.JBO.25.9.097003.full?fbclid=IwAR02-l_q-xCykuuqUjc_RWJfQE7ESOEIRK0G9mqZSWaGiFhfwu1QNV42vjQ&SSO=1 (https://www.spiedigitallibrary.org/journals/journal-of-biomedical-optics/volume-25/issue-09/097003/Diffuse-correlation-spectroscopy-measurements-of-blood-flow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)

Zeff et. al. “Retinotopic mapping of adult human visual cortex with high-density diffuse optical tomography” National Academy of Sciences. 2007
https://www.pnas.org/content/104/29/12169

Anwar. “Scientists use brain imaging to reveal the movies in our mind” Berkeley News. 2011. https://news.berkeley.edu/2011/09/22/brain-movies/

Shen, Horikawa, Majima, Kamitani. “Deep image reconstruction from human brain activity” PLOS Computational Biology. 2019. https://journals.plos.org/ploscompbiol/article?id=10.1371/journal.pcbi.1006633

Wang et. al. “CNN Explainer” Github. 2020.
https://github.com/poloclub/cnn-explainer

Wang et. al. “CNN Explainer: Learning Convolutional Neural Networks with Interactive Visualization” IEEE VIS 2020. (2020)
https://arxiv.org/abs/2004.15004

O’Sullivan, Hoffman, Paulson. “Reality is Not As It Seems” New York Academy of Sciences. 2019. https://www.youtube.com/watch?v=3MvGGjcTEpQ

Gratton, Fabiani. “Chapter 15, Fast Optical Signals: Principles, Methods, and Experimental Results” In Vivo Optical Imaging of Brain Function. 2009. https://www.ncbi.nlm.nih.gov/books/NBK20223/#:~:text=Fast%20optical%20signals%20are%20rec ently,through%20the%20intact%20human%20brain. (https://www.ncbi.nlm.nih.gov/books/NBK20223/)

Espigares et al. “Assessment of natural enamel lesions with optical coherence tomography in comparison with microfocus x-ray computed tomography” Journal of Medical Imaging. 2015. https://pubmed.ncbi.nlm.nih.gov/26158079/

Su et. al. “Imaging the anterior eye with dynamic-focus swept-source optical coherence tomography” Journal of Biomedical Optics. 2015
https://pubmed.ncbi.nlm.nih.gov/26662065/

“Wim Hof” Wikipedia. 2020.
https://en.wikipedia.org/wiki/Wim_Hof

Herrero, Khuvis, Yeagle, Cerf, Mehta. “Breathing above the brain stem: volitional control and attentional modulation in humans.” Journal of Neurophysiology. 2018. https://journals.physiology.org/doi/full/10.1152/jn.00551.2017

Jhang et. al. “Anterior cingulate cortex and its input to the basolateral amygdala control innate fear response.” Nature Communications. 2018. https://www.nature.com/articles/s41467-018-05090-y

Moberly et. al. “Olfactory inputs modulate respiration-related rhythmic activity in teh prefrontal cortex and freezing behavior” Nature Communications. 2018. https://www.nature.com/articles/s41467-018-03988-1

Riachle, Gusnard. “Appraising the brain’s energy budget” National Academy of Sciences. 2002. https://www.ncbi.nlm.nih.gov/pmc/articles/PMC124895/

Kuzawa, Blair. “A hypothesis linking the energy demand of the brain to obesity risk” National Academy of Sciences. 2019.
https://www.pnas.org/content/116/27/13266

Tata, Ruhrberg, Fantin. “Vascularisation of the central nervous system” Mechanisms of Development. 2015.
https://www.ncbi.nlm.nih.gov/pmc/articles/PMC4678116/

Kim, Park, Choi. “The Role of Astrocytes in the Central Nervous System Focused on BK Channel and Heme Oxygenase Metabolites: A Review” Antioxidants. 2019. https://www.ncbi.nlm.nih.gov/pmc/articles/PMC6562853/

Marina et. al. “Astrocytes monitor cerebral perfusion and control systemic circulation to maintain brain blood flow” Nature Communications. 2020. https://www.nature.com/articles/s41467-019-13956-y

Mirgain et. al. “Whole Health: Change the Conversation. The Power of Breath: Diaphragmatic Breathing Clinical Tool” Veteran’s Health Affairs. 2016 http://projects.hsl.wisc.edu/SERVICE/modules/12/M12_CT_ThePowerOfBreathDiaphragmaticBr eathing.pdf (http://projects.hsl.wisc.edu/SERVICE/modules/12/M12_CT_ThePowerOfBreathDiaphragmaticBreathing.pdf)

Peteri, Niukkanen, Castren. “Astrocytes in Neuropathologies Affecting the Frontal Cortex” Frontiers in Cellular Neuroscience. 2019. https://www.ncbi.nlm.nih.gov/pmc/articles/PMC6379461/#:~:text=Astrocytes%20comprise%20of %20a%20heterogeneous,region%20especially%20susceptible%20to%20damage. (https://www.ncbi.nlm.nih.gov/pmc/articles/PMC6379461/)

Tatsumi et. al. “Voluntary Exercise Induces Astrocytic Structural Plasticity in the Globus Pallidus” Frontiers in Cellular Neuroscience. 2016.
https://www.ncbi.nlm.nih.gov/pmc/articles/PMC4914586/

Lin, Tsai, Kuo. “Physical Exercise Enhances Neuroplasticity and Delays Alzheimer’s Disease” Journal of Brain Plasticity. 2018
https://www.ncbi.nlm.nih.gov/pmc/articles/PMC6296269/

Ballard. “Exercise makes your brain bigger: skeletal muscle VEGF and hippocampal neurogenesis” Journal of Physiology. 2017.
https://www.ncbi.nlm.nih.gov/pmc/articles/PMC5577549/

Takano et. al. “Astrocyte-mediated control of cerebral blood flow” Nature Neuroscience. 2006. http://www.cns.nyu.edu/events/spf/SPF_papers/takano_etal_2006.pdf

Fenoy, Goetz, Chabardes, Xia. “Deep Brain Stimulation: Are Astrocytes a Key Driver Behind the Scene?” CNS Neuroscience & Therapeutics. 2014. https://www.ncbi.nlm.nih.gov/pmc/articles/PMC3969941/

Eagleman. “Can we create new senses for humans?” TED. 2015. https://www.ted.com/talks/david_eagleman_can_we_create_new_senses_for_humans?language=en

Novich, Eagleman. “Using space and time to encode vibrotactile information: toward an estimate of the skin’s achievable throughput” Experimental Brain Research. 2015. https://link.springer.com/article/10.1007/s00221-015-4346-1

Reiter, Anderson, Carlsson. “Neurofeedback Treatment and Posttraumatic Stress Disorder” The Journal of Nervous and Mental Disease. 2016. https://www.csusb.edu/sites/default/files/upload/file/2016_Reiter%2C%20Andersen%2C%20Carlsson_Neurofeedback%20Treatment%20and%20PTSD_0.pdf (https://www.csusb.edu/sites/default/files/upload/file/2016_Reiter%2C%20Andersen%2C%20Carlsson_Neurofeedback%20Treatment%20and%20PTSD_0.pdf)

Areces et. al. “Using Brain Activation (nir-HEG/Q-EEG) and Execution Measures (CPTs) in a
ADHD Assessment Protocol” Journal of Visualized Experiments. 2018. https://pubmed.ncbi.nlm.nih.gov/29658934/

“Guidelines for SpO2 using the MAXIM MAX32664 Sensor Hub” MAXIM Integrated. 2019 https://www.maximintegrated.com/en/design/technical-documents/app-notes/6/6845.html

Sukhoruchkin, Brewster, Markus. “FreeEEG32” Crowd Supply. 2020 https://www.crowdsupply.com/neuroidss/freeeeg32

Brewster, “DIY Diffuse Optical Tomography” Github. 2020. https://github.com/moothyknight/DIY_DOT

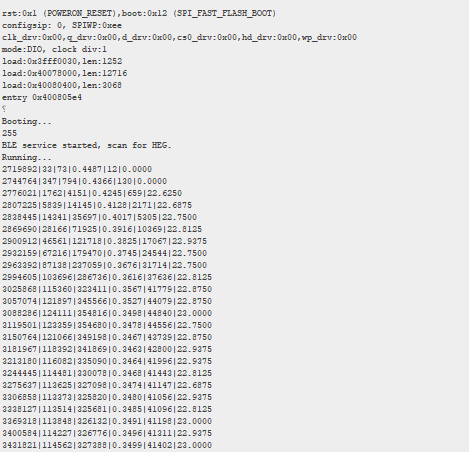
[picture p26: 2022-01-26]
Designs/MAX86141HEG/Data.PNG

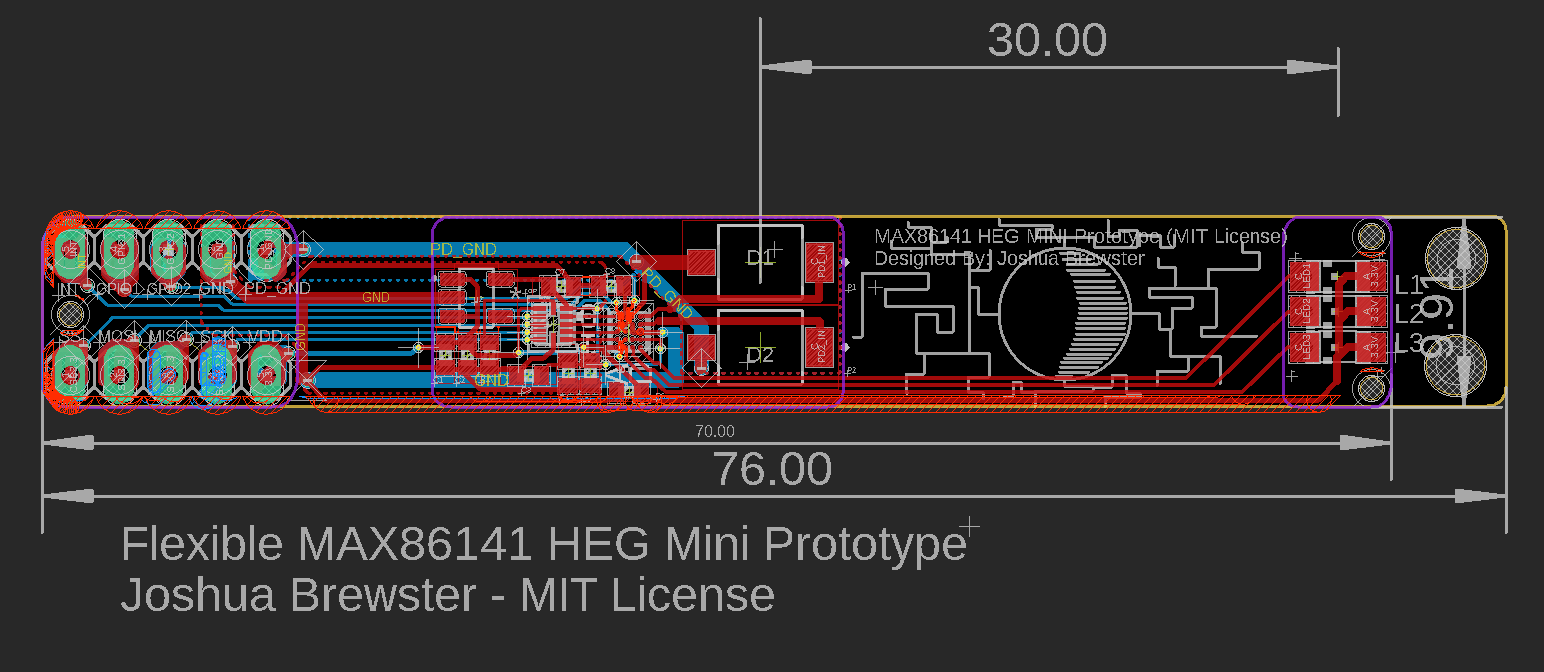
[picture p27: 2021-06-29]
Designs/MAX86141HEG/Breakout.PNG

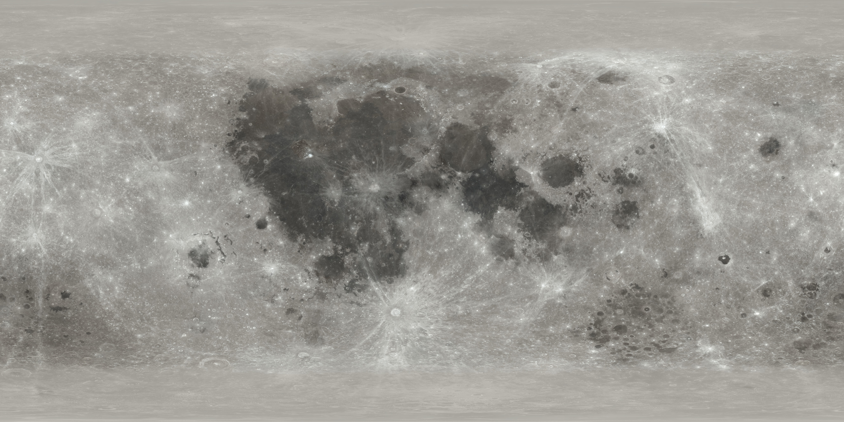
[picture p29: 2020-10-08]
ChromeExtension/assets/textures/moon_4k.jpg

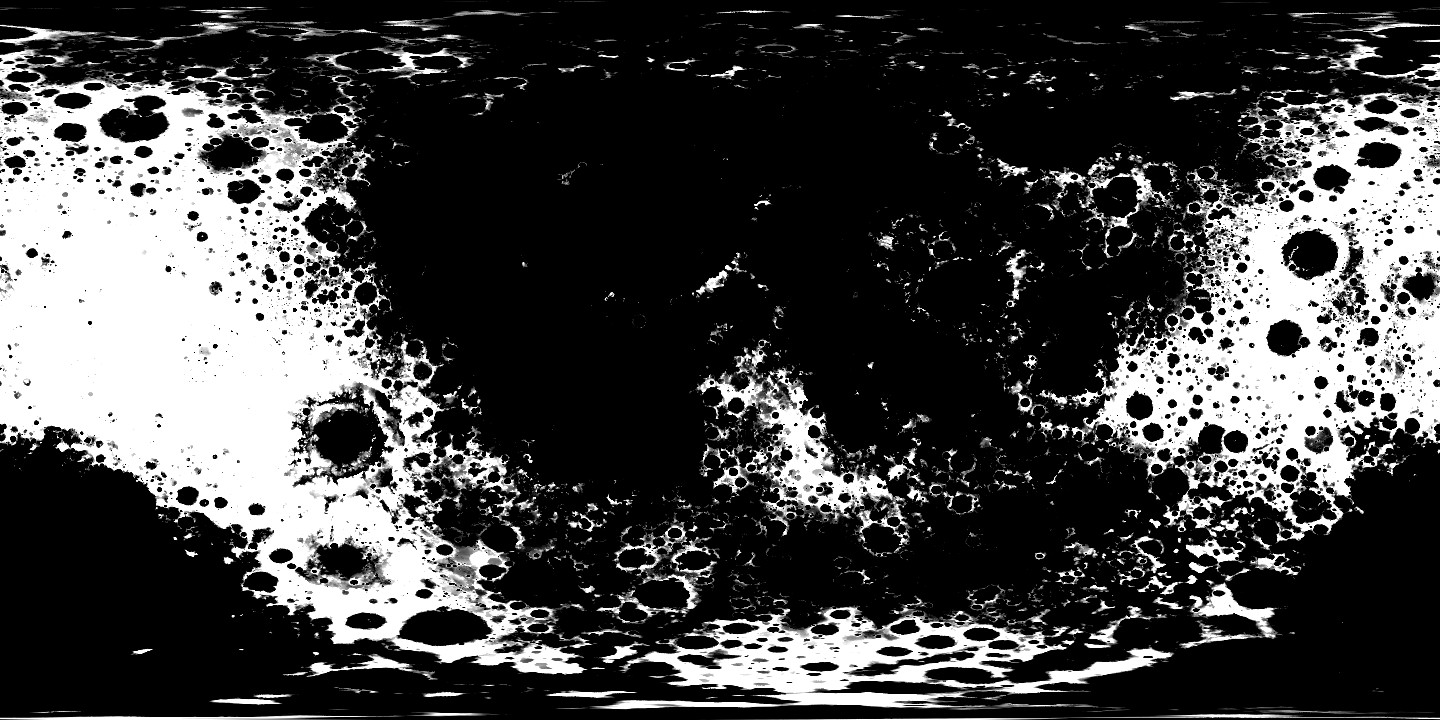
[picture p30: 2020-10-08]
ChromeExtension/assets/textures/moon_displace_4k.jpg

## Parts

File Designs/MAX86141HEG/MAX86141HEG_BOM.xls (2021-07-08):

Id | Designator | Package | Qty/unit | Designation | More Info | Digikey Cost | 1 | 10 | 100 | 1000
1 | U1 | 20 Bumps Thin WLP | 1 | MAX86141ENP+T | https://pdfserv.maximintegrated.com/package_dwgs/21-100134.PDF |  | 7.38 | 66.65 | 551.8 | 4185
2 | D1,D2 |  | 2 | BPW 34 S-Z | https://www.mouser.com/ProductDetail/OSRAM-Opto-Semiconductors/BPW-34-S-Z?qs=K5ta8V%252BWhtbaD%252B%252BL55sGPw%3D%3D |  | 1.02 | 6.65 | 43.57 | 435.7
3 | L1 | 1206 | 1 | XZTHI55W-3 | LED Indication - Discrete 1.2V 1206 (3016 Metric) 880nm
4 | L2 | 1206 | 1 | XZTNI55W-3 | LED Indication - Discrete 1.2V 1206 (3016 Metric) 940nm |  | 0.5 | 3.61 | 23.56 | 132.5
5 | L3 | 1206 | 1 | XZM2MR55W-3 | LED RED CLEAR 3216 SMD 660nm |  | 0.48 | 3.41 | 19.88 | 113.62
6 | C4,C6 | C0402 | 2 | GRM155R60G106ME44D | Multilayer Ceramic Capacitors MLCC - SMD/SMT 0402 10uF 4.0volts X5R 20% |  | 0.2 | 1.36 | 6.9 | 41.77
7 | C1,C2,C3,C7,C8 | C0402 | 5 | EMK105BJ105MVHF | Multilayer Ceramic Capacitors MLCC - SMD/SMT 0402 16VDC 1uF 20% X5R AEC-Q200 |  | 0.1 | 0.46 | 2.05 | 11.5
8 | C5 | C0402 | 1 | EMF105B7104MVHF | Multilayer Ceramic Capacitors MLCC - SMD/SMT 0402 16V 0.1uF 20% AEC-Q200 CER 0.1UF 6.3V X5R 0603 |  | 0.18 | 1.26 | 5.94 | 34.5
9 | R1 | R0402 | 1 | RG1005P-103-D-T10 | Thin Film Resistors - SMD 1/16W 10K Ohms 0.5% 0402 25ppm |  | 0.14 | 1.27 | 4.9 | 21.56
10 | U2 | SOT-23-5 | 1 | LP5907MFX-1.8/NOPB | LDO Voltage Regulators 250mA Ultra-Lo Noise LDO Reg |  | 0.55 | 4.31 | 32 | 191
11 | U3 |  | 1 | TXBN0304RUTR | 3.3v to 1.8V bidirectional 4-channel voltage regulator
 |  |  | 17 |  |  | TOTALS | 10.55 | 88.98 | 690.6 | 5167.15

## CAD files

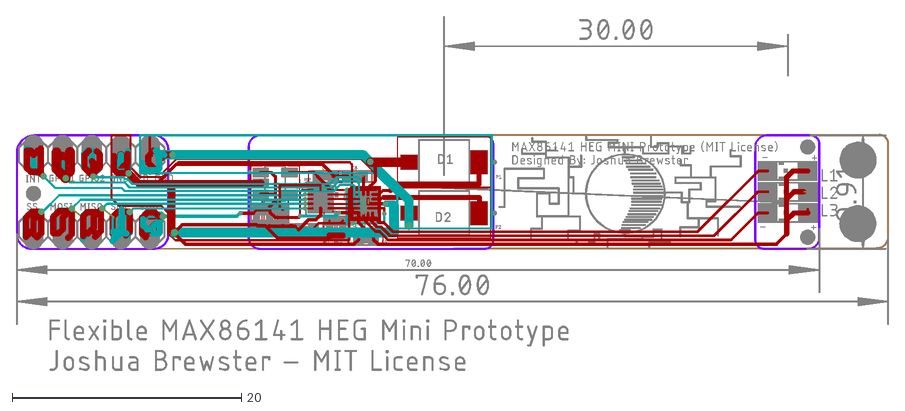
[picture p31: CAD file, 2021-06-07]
Designs/MAX86141HEG/MAX86141_HEG_MINI.dxf
76.2 x 30.9

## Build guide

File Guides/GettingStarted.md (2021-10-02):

## So you just got your device

### Quick Start
* Open this new improved app https://app.brainsatplay.com or the old app demo via Chrome: https://hegalomania.netlify.app 
* You can install it by clicking the settings icon (3 vertical dots) in the top right corner. It will be automatically kept up to date as long as your device is connected to the internet.
* Enable Serial by entering chrome://flags in a new tab and enabling the "Experimental Web Platform Features" flag and restarting Chrome when prompted.
* Plug in your HEG via USB, you should see it flashing then show solid red (if you don't see the LED, reset the device by unplugging it or feeling around for the reset button in the middle of the microcontroller hub) 
* Connect your device via "Set USB Device." Data should begin streaming in automatically. If not, reset the device. There are some known glitches on startup here.
* With the device on your head, you can squeeze and bend the headset until it is comfortable on your head. You don't need to wear it so tight that you feel like you are being poked by the LEDs or gripped by the headset, it should be comfortable.
* If the data looks funky or random, make sure the fabric on the headband is not covering the sensor, which should be in contact with your forehead.



#### Web Interface
* The device should boot up in WiFi mode by default. This is indicated by 3 quick flashes in succession upon reset. After that you will see 3 slower flashes. Resetting after the first slower flash will change the communication mode (2 for BLE, 3 for WiFi, 4 for BT Serial). Use BLE mode for mobile.
* Find the WiFi connection "My_HEG" and enter password 12345678
* Open a browser (Chrome preferably) and enter [http://192.168.4.1](http://192.168.4.1) or [http://esp32.local](http://esp32.local) if that doesn't work

### Quick Training Guide
* The ratio represents the relative blood-oxygen content in your brain. A higher ratio represents a higher relative blood-oxygen saturation in your brain tissue. The score is simply an exaggerated ratio with the baseline 0 point set at the initial ratio. The different visuals (accessible via the Feedback menu) react to the score. You can reset the session via the Reset button in the Data menu.
* Simply perform a 6 breath per minute (5 seconds in, 5 seconds out), deep cyclical breathing exercise for 5-15 minutes (no pauses, just do a chest-expanding, relaxing inhale and exhale wave pattern). Stop if you feel any strain.
* Once your breathing is stabilized, try to notice what thoughts or distractions come up and see if you notice any correlation with the change in score or ratio on-screen. You may quickly find that stress and focus can have a big effect on the patterns, it may take a few sessions to notice.
* Use the combination of stable breathing and awareness of your own thoughts to try to optimize the increase in your score. Your ratio will only increase so much before going back to baseline, which is your brain doing work then relaxing again. You may even feel fatigue when this occurs, which is a good indicator you're doing it right and to take a break.

### Important
* Keep the LEDs away from your eyes, you can even give yourself a headache from eye strain with the light passing through your skull if it's too close, so keep it higher on your forehead or to the side of your head.
* Speak to an expert before using this for headaches or migraines. Our development kit is not rated for medical use nor are any HEGs, so proceed with caution.

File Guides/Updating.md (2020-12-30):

### Updating your device

This is a pretty simple process, just follow these steps:
* Download the latest Delobotomizer_Update_##_##_##.bin by navigating to it it in this repository and pressing the "Download" button over the file.
* Log into the WiFi signal produced by the device "My_HEG" with password 12345678
* Open your browser (Chrome preferred) and enter the address [http://192.168.4.1/update](http://192.168.4.1/update) or [http://esp32.local/update](http://esp32.local/update).
* Follow the prompts and upload the .bin file you just downloaded, wait a couple minutes for the device to reset and it's up to date!

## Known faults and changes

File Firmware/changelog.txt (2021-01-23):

*-*-*-*-*-*-*
Changelog:
*-*-*-*-*-*-*
1/23/21
------
- BLE fix
- filter tweaks 

1/21/21
------
- Noise B gone! Implemented notch and low pass filtering (3x 50Hz notch,3x 60Hz notch, and 3x 40Hz low pass). AC will never bother you again. I should up the output sampling rate again.
- MASSIVE upgrade to the software coming soon
- 'F' command toggles filters. 'X' command toggles a DC filter. 

12/8/20
------
- Boot sequence better fix, red led is the indicator now. If you don't see the blinks when you power it, reset the device.
- css adjustments

12/3/20
------
- fix to boot sequence not always running the sensor

11/1/20
------
- Increased exposure time of LEDs to 58.7uS (slightly brighter signal), halved sample average (16 samples @ 2048 sps)
- fixed "f" command.

10/31/20
------
- Boids update, new feedback mode
- Some cleanup to the UI
- BLE mode cleaned up and support enabled in the chrome extension. "o" for fast output mode (for android web's 20 byte packet maximum)
- Check out hegalomania.netlify.app for a mobile progressive webapp WIP demo.

10/23/20
------
- Convenience update! Device now flashes on boot and lets you toggle different things just with the reset button. The first flashes are in rapid succession. 2 flashes = BLE mode, 3 flashes = WiFi mode, 4 flashes = BT Serial (classic) mode. Then the device will give 3 slow blinks (once per second) after that.
- If you press the reset button again within the first 3 seconds (1 flash per second) that triggers different things.
- Press after rapid flashes and before first slow flash (first second): places device in deep sleep mode.
- Press after first slow flash, before second slow flash: (2nd second: change the communication mode (rotates between BLE, WiFi, and BT Serial)
- Press after second slow flash, before third slow flash (3rd second): wipes saved wifi credentials in case there is some issue.

- BLE connectivity added to extension. Now developing progressive webapp for mobile. 

10/14/20
------
- Updated the stream format to fit the Delobotomizer
- Fixed the web interface not appearing (had an extra 'undefined' in the session initialization)

7/16/20
------
- Generalization: One-liners and commands to control device stream format compatibility e.g. different delimiters and ratio or timer positions, this auto propagates to the CSV recording as well.
- Other cleanup, getting ready for more feature updates.

6/2/20
------
- reverted CSV function in HEGwebAPI (it has the new one too, just not dumping raw data due to noise issues)
- fixed Chrome extension csv printing for serial and bluetooth

6/1/20
------
0.0.10
- Reworked audio system for the AudioJS, fixed the audio feedback (not sure how I broke it!)
- 2 more audio visualizers
- better colors on CircleJS
- tweaked Hill Climber
- Generalized the CSV function
- SoundJS has a recording function you can use, default set for audio recording but can do video, requires a SoundJS class to be set (either when audio is active or through the console)
- SerialUtils.js for the Chrome Extension now has recording and monitoring functions (the monitor is not set up yet on the front end)
- Separated the javascript on the webDemo.html into initWebapp.js for parity with the Chrome Extension
- geolocateJS created for an interesting project

TODO: 
- Make performant serial monitor front end, 
- geolocate.js interactive features - heat maps!
- work on BCIjs integration for EEG data (I need to get ahold of one with a generic data stream) on extension, 
- more visuals, 
- better recording menu.

5/26/20
------
0.0.9
- Added a Sound scripting system, allows arrays of frequencies and sound files to be buffered and used individually.
- Added sound options to HillJS and CircleJS, just simple tones to help indicate the feedback.
- Added a new mode to HillJS, it looks a lot nicer now.
- Some minor fixes

5/1/20
------
- Fixed BLE output format, optimized general output method

4/3/20
------
- USB only mode introduced via command 'u' or toggling on the Connections Settings page at 192.168.4.1/connect or esp32.local/connect
- Fixed the autoscaling on negative graph values (there was none, oops)
- General stability testing, everything seems OK, get your device up to date!

3/28/20
------
- Tooltips!
- New Video mode, control the current time of the video just like HEGstudio! It's officially obsolete. No sound in this mode, but it would probably sound pretty bad.

3/26/20
------
- Fixed the HTML5 page code (didn't paste it correctly)
- Added sleep mode, now the device shuts off after 10 minutes of inactivity. It won't shut off if you are accessing web pages or running the core program, or updating. To turn it back on simply press the reset button or re-plug the power in. This will get more sophisticated to allow remote waking-up.

3/24/20
------
- Reintroduced Bluetooth Serial (surprisingly low footprint on top of BLE). Works like standard USB but requires pairing first. 2 Com ports show up for me when enabled, you want the first one. The one that lets you send commands is the one you want.
- Some bug fixes
- Working on a new video feedback mode
- Separate changelog

3/20/20
------
- Fixed EventSource stream for remote streaming. Updated UI for the changes.
- Added a TextReader feedback option.
- Chrome Extension port of webAPI, with Serial USB support coming. Much easier to code bigger apps in this.
- Microsoft Edge beta supports this UI, and might support the Chrome Extension too.

3/14/20
------
- Added more BLE commands
- Re-added alternative ADS1115 library setup, which is fully programmable up to the full sampling rate (with variable consistency in the data)

3/2/20
------
- Updated SMA function, added basic fault testing for ratio (within 25% error)
- Fixed Annotating
- Some minor tweaks here and there
- DataCharter.html introduced, it's IFrame-ready and meshes with JSON, will soon also be loaded as an online-only option for the firmware. See it in action at hegalpha.com/data (account required)

2/26/20
------
- Fixed yoffset slider (changed a + to a - for the y-axis text)
- Timer now shows minutes and seconds proper.
- Touched up Update page
- Touched up ThreeJS demo colors

2/20/20
------
- Added a formal Reset Session button (instead of reloading page)
- Seconds passed approximation in graph.
- ThreeJS demonstration is even prettier now. 

2/19/20
------
- Added postprocessing fx to threejs demo
- More code cleanup.

2/18/20
------
- Major improvements to code flow
- Conditional ThreeJS integration (auto detects if you are online or not and attempts to add Three.js.min)
- Globe turning exercise to demonstrate ThreeJS and how easy modding is.
- Other minor fixes to feedback and UI.
- Updated env to latest ESP32 release.

2/14/20
------
- Y offset slider
- Fixed fade mode (the CSS needed tweaking)

2/13/20
------
- Exposed method to change event source hosts, for clients not hosted on-board but still on the same network. This opens up more web development capabilities.
- Scoring sensitivity slider can now got to X10, though this is pretty unnecessary.

2/11/20
------
- Graph can now be switched between the score and ratio
- Added Timestamped annotating that will show up in the session CSVs
- Fixed one thing with the x scale slider, the graph crash bug is still there
- Some other API rearrangements

2/7/20
------
- AudioJS options - volume slider and an option for decoupling the volume feedback.
- Fixed HillJS. It's not that great but it's a bit more responsive than before. I need to add more compelling visual feedback.
- Index page update
- Timer actually shows the session time and not the microcontroller clock
- More UI cleanup

2/6/20
------
- Major improvements to UI layout
- API improvements for better generalization (still WIP)
- Custom video controls, show/hide controls
- CircleJS, AudioJS, and HillJS touched up. HillJS is basically unresponsive but I'm working on it next.
- Some cleanup
- IE/Edge will not be supported by the on-board training demos until it is updated to ES8 standards (due to lack of arrow functions, mainly) or until I or others make compatible scripts, still need to test more mobile compatibility as well as understand why some laptops are not compatible.

1/31/20
------
- Minor changes and fixes to UI and javascript

1/22/20
------
- Major mobile-friendly UI updates to web interface page (Alpha 0.0.1 for the interface)
- Changes to data outputs (replaced rSlope and A.I. with velocity and acceleration (voltage units / ms and voltage units / ms ^2). 1 ADC unit = 0.256mV so if Vel = 1 that's +0.256mV gained per millisecond
- Cleanup of HEG.h code.
- Testing notes: 
   -- Some power sources cause unstable readings. Try different power sources.
   -- Different computers/phones seem to have different compatibility errors for the same software (e.g. one laptop not working with Microsoft Edge and another one working great) - not totally sure why.
12/16/19
------
- updated front page, connection page, and help page. Now with version number visible on main page.
- the web API lets you set an arbitrary host for the event source now for quicker remote play (set host with a new HEGwebAPI(parentId,defaultUI,**hostIP**))
 
12/14/19
------
- Made standalone /api page with uninitialized JS api and CSS available for external use.

12/10/19
------
- Rolled back ADC library due to too much instability.

12/8/19
------
- Fixed sampling issues. Now doing 3 samples per LED (and ambient) for 20sps solid over USB, WiFi, and BLE.
- Fixed BLE (thanks Diego!)

12/3/19
------
- Changed ADS1115 libraries to the addicore version (via on i2cdevlib)
- Upped sample rate to 475sps, ratio rate (with ambient cancellation) should now be ~133 at full speed over Serial.
- Fixed Serial commands not being responsive
- Removed "T" test command for now.

11/25/19
------
- fix LEDs not shutting off when pausing HEG
- lowered power consumption
- fixed circleJS in web API

Known bugs:
- Serial USB commands don't register very well 
- ADC anomalies with WiFi (probably power consumption related)
- xOffset bugged when changing xScale and xOffset together

To Do:
- Use a better ADS1115 lib to improve speed
- Web Demo CSS and functionality improvements
- IE and Edge can't find the HEGwebAPI.js script (this is likely the same issue on mobile)

11/11/19
------
- fix web api and hegstudio to match changes

11/9/19
------
- removed sav lay filter (do it on front end instead after checking data)

11/4/19
------
- ADC error check in HEG.h (to deal with a webserver bug), use 'A' to toggle. 
- Add progress events for /update page.

KNOWN BUGS:
The error checker can cause hangups and overheat the chip, don't use it yet

11/3/19
------
-webDemo now filters bad data out for a smoother experience, to compensate for a bug mainly
-testing threading to try to fix wifi data streaming errors. Turn sensor off and on if connecting online while sensor is active. (very particular not often-gonna-happen bug)

Known bugs:
The wifi connection causes errors in the ADC readings for some reason, need to fix this
to make the sav lay filters usable over web.

10/29/19
------
-/discovery page for testing device scanning from mobile
-Reimplemented ambient noise cancelling and added a read_differential mode. Works much better like this, closer to the original!
-/help page (BIG work in progress)

10/21/19
------
-connect page now has a suggest IP option. Return to the /connect page after reconnecting to the access point.
If it works correctly you get booted to the main page and can go straight to the /connect page again, scroll down, and see the suggested info above the wifi scan text.
-proof of concept hill climb game
-more cleanup (not all the way there yet)

More to do:
Audio mode that just plays a tone that gets louder or quieter? 
Device search on local wifi when in STA mode.
More controls for modes.

10/18/19
------
-integrated audio mode
-added volume feedback for video option
-code feng shui improvements

FYI: not all buttons hooked up yet

Known bugs:
-not every browser works on canvas demo
-poor audio quality on visualizer mode - try manual buffering. Bug not present in standalone visualizer.
-offset button bugged when offsetting more than the number of graph vertices (look at xoffsetSlider.onclick setting)

10/17/19
------
smooth mode switching on demo page. Audio and hill climbing (LIFE game re-creation) games incoming.
change graph to show cumulative SMA 1s - 2s slope changes. This math is a simple noise filter that is still reactive to the current information, which can overcome noise issues. 
split code up into multiple files to fit a cleaner traditional webapp format.
web api improving and generalizing rapidly
can set primary/secondary dns if needed, smart config type stuff incoming.

couple bugs:
X offset slider still, it's 3 lines of code causing a problem.
the replay function works fine but goes over the index when resetting the data. This bit will be re-done as the code is spaghetti.

10/14/19
------
-x offset bar. Has a bug when offsetting when graph scale is lower than the array being sliced. page has to be reloaded if red line vanishes.
-Even classier, almost finished streamlining code.
-integrated hegvid code with main page, need to create options to swap once finished generalizing the data handling. this will be smoooooth

10/13/19
------
webGL graphing API improvements. More to come.
WIP Object-oriented web API on canvas demo page. Final suite will be completely class-based.
Sensitivity slider.
/hegvid -> /video (this page will be integrated with the main demo)

More TODO:
Audio visualizer (HTML5 has sweet built-in tools)
CSS Overhaul w/ animations. Utilize webkit/moz/mobile libs.
Fix mobile support for web demo (mostly requires permissions changes)

10/11/19
-----
/hegvid page improvements/experiments. Can load local video files (web URLs next, some site embedding like Vimeo MIGHT work)

10/10/19
-----
CSV Save/Load functions added.
Graphing improved, canvas demo fairly playable now. 
Waiting on new pcbs to get definitive data after fixing noise issues in designs.
GraphJS wrapper class for graphing.

TODO:
graph upgrades
reformat functions and variables into respective classes to reduce bloat.
sliders for exploring data
create SPIFFS js packages? That way we can break up essential functions on the webAPI and reduce bloat or add third party packages easily.
hegstudio brightness exercise recreation is easiest to do with default <video> tag and a transparency overlay.
Fix spaghetti

10/6/19
-----
Fixed crash when changing wifi modes
Add static IP settings. 
Working on WebGL based graphing and video controls. /hegvid wip

10/1/19
------
Canvas demo
Really basic navigation on index page
Fix websocket page to use js to call the hostname in case of esp32.local being used.
More POST commands, also added text input-based command method as an option, only send single char.

9/9/19
------
EventSource works great!

More TODO:
Make connect page notify the user of the new IP address if esp32.local is not fixed.
Convert websockets to drive commandESP32

9/5/19
------
TODO:
Data visualizer. HEG Life game in canvas?
Stress testing - try EventSource instead of Websockets. Websockets can overflow and crash the ESP32 easily if there is lag clientside.
Login interface?
HTML interface to use commandESP32

9/5/2019
------
Fixed OTA, update boards.txt and default.csv in their respective folders (see above install instructions)
Changed setup loop so wifi is always chosen if EEPROM.read(0) is not 1 for BLE.

9/3/19
------
Included BLE support. toggle BLE/WIFI with 'b', BLE default off due to conflict with WiFi
Websockets and HEG now on separate threads so sensor speed is not impacted - WS speed set at 13.33 updates/sec as it's stable. Max = 16/sec
/update broken. Gotta fix it.
Lots of housekeeping to keep workflow easy, tested the freeRTOS threading system a ton.
commandESP32 now in WiFi_API.h.

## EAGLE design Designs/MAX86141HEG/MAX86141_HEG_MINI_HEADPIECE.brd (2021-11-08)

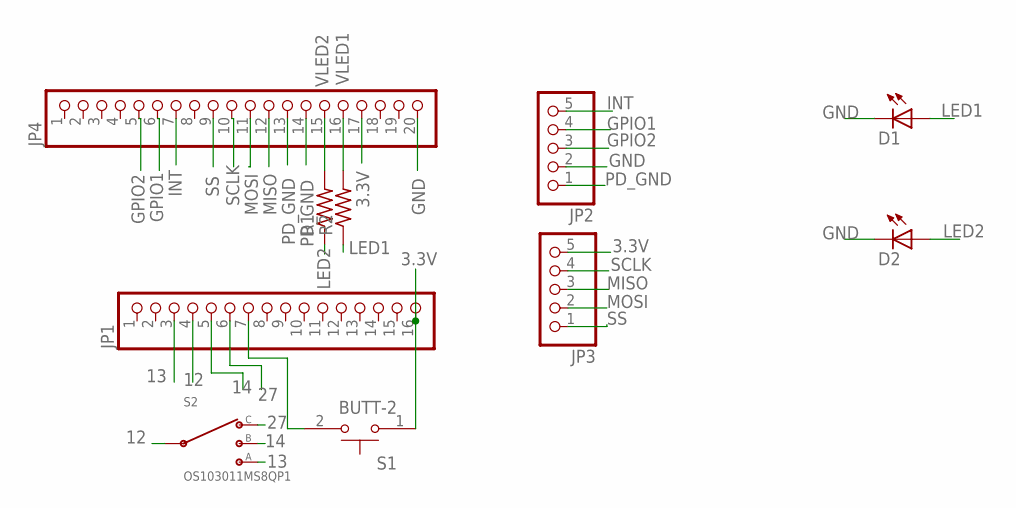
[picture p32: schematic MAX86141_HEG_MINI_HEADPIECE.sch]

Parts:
D1, D2: LED1206; LED-1206
JP1: PINHD-1X16; 1X16
JP2, JP3: PINHD-1X5; 1X05
JP4: PINHD-1X20; 1X20
R1, R2: R-US_0204/5; 0204/5
S1: BUTT-2; SW_BUTT-2
S2: OS103011MS8QP1; OS102011MS8QP1

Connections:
3.3V: JP1.16, JP3.5, JP4.17, S1.1
12: JP1.4, S2.2 (C)
13: JP1.3, S2.1
14: JP1.5, S2.3 (2)
27: JP1.6, S2.4 (3)
GND: D1.C, D2.C, JP2.2, JP4.20
GPIO1: JP2.4, JP4.6
GPIO2: JP2.3, JP4.5
INT: JP2.5, JP4.7
LED1: D1.A, R2.1
LED2: D2.A, R1.1
MISO: JP3.3, JP4.12
MOSI: JP3.2, JP4.11
unnamed: JP1.7, S1.2
PD_GND: JP2.1, JP4.13, JP4.14
SCLK: JP3.4, JP4.10
SS: JP3.1, JP4.9
VLED1: JP4.16, R2.2
VLED2: JP4.15, R1.2

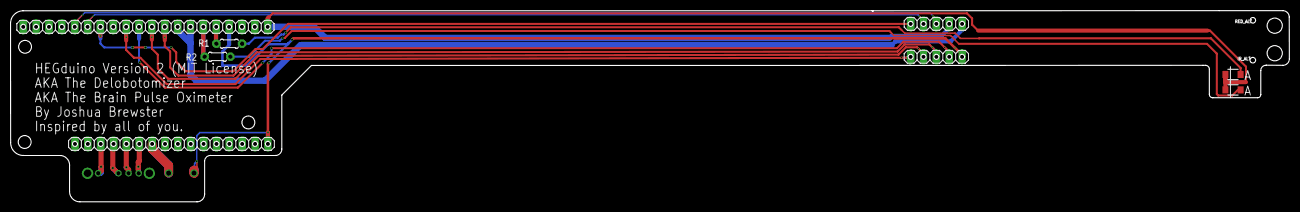
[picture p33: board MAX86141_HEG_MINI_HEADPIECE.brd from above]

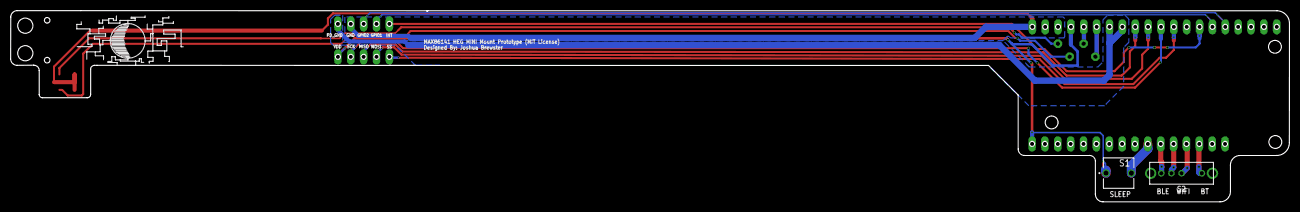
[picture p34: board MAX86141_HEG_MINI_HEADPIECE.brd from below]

Board: 2 copper layers, 252.5 x 37.7 mm, 10 parts (2 on the bottom side), 19 nets.

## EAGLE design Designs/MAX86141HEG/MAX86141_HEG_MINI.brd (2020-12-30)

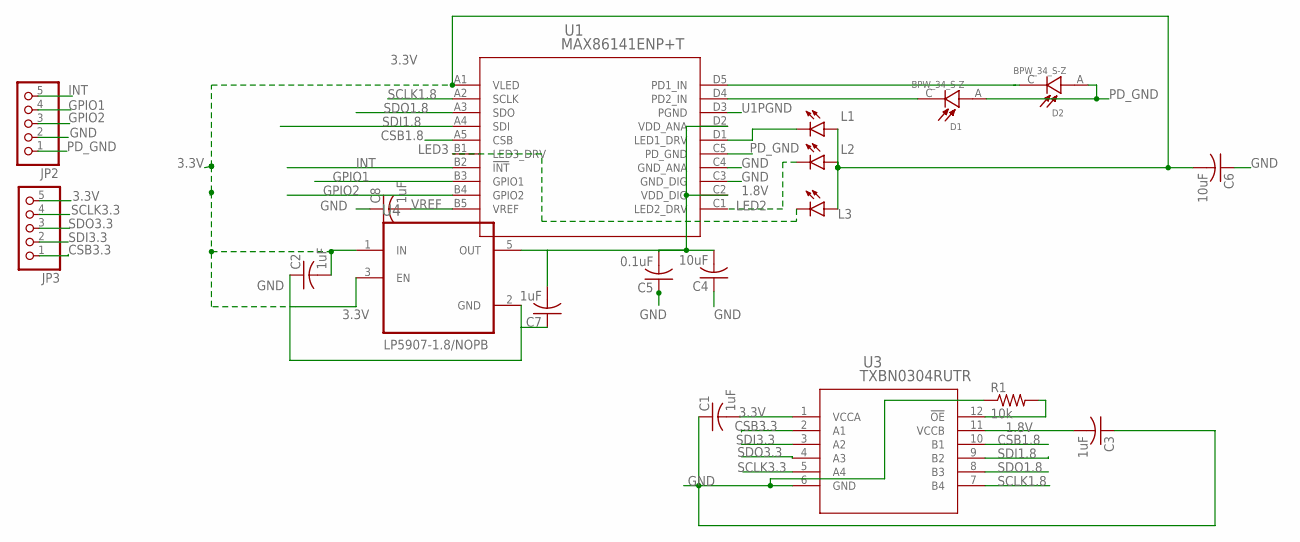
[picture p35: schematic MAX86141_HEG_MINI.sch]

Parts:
C1, C2, C3, C7, C8: 1uF; C0402
C4, C6: 10uF; C0402
C5: 0.1uF; C0402
D1, D2: BPW_34_S-Z; DIO_BPW_34_S-Z
JP2, JP3: PINHD-1X5; 1X05
L1, L2, L3: LEDCHIPLED_1206; CHIPLED_1206
R1: 10k; R0402
U1: MAX86141ENP+T; 21-100134A_20
U3: TXBN0304RUTR; RUT12
U4: LP5907MFX-3.3/NOPB; SOT95P280X145-5N

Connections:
1.8V: C3.2, C4.2, C5.2, C7.2, U1.C2 (VDD_DIG), U1.D2 (VDD_ANA), U3.11 (VCCB), U4.5 (OUT)
3.3V: C1.2, C2.2, C6.2, JP3.5, L1.A, L2.A, L3.A, U1.A1 (VLED), U3.1 (VCCA), U4.1 (IN), U4.3 (EN)
CSB1.8: U1.A5 (CSB), U3.10 (B1)
CSB3.3: JP3.1, U3.2 (A1)
GND: C1.1, C2.1, C3.1, C4.1, C5.1, C6.1, C7.1, C8.1, JP2.2, R1.1, U1.C3 (GND_DIG), U1.C4 (GND_ANA), U3.6 (GND), U4.2 (GND)
GPIO1: JP2.4, U1.B3 (GPIO1)
GPIO2: JP2.3, U1.B4 (GPIO2)
INT: JP2.5, U1.B2 (!INT)
LED1: L1.C, U1.D1 (LED1_DRV)
LED2: L2.C, U1.C1 (LED2_DRV)
LED3: L3.C, U1.B1 (LED3_DRV)
OE: R1.2, U3.12 (!OE)
PD1_IN: D2.C, U1.D5 (PD1_IN)
PD2_IN: D1.C, U1.D4 (PD2_IN)
PD_GND: D1.A, D2.A, JP2.1, U1.C5 (PD_GND)
SCLK1.8: U1.A2 (SCLK), U3.7 (B4)
SCLK3.3: JP3.4, U3.5 (A4)
SDI1.8: U1.A4 (SDI), U3.9 (B2)
SDI3.3: JP3.2, U3.3 (A2)
SDO1.8: U1.A3 (SDO), U3.8 (B3)
SDO3.3: JP3.3, U3.4 (A3)
U1PGND: U1.D3 (PGND)
VREF: C8.2, U1.B5 (VREF)

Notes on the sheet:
LP5907-1.8/NOPB

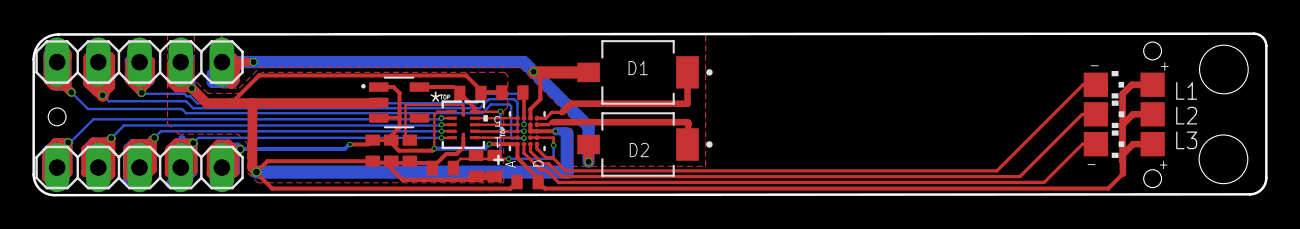
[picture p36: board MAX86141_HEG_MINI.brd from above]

Board: 2 copper layers, 76.0 x 10.0 mm, 19 parts (0 on the bottom side), 22 nets.

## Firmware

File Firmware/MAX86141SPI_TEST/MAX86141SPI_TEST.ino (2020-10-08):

#include "MAX86141.h"

#include <esp_timer.h>

static int spiClk = 1000000; // 8 MHz Maximum

unsigned long currentMicros;
unsigned long LEDMicros;
unsigned long LEDFrequency = 7500; //Time (in Microseconds) between each change in LED state (Red, IR, Ambient);

bool RED_ON = false;
bool IR_ON = false;
bool AMBIENT = true;

float RED_AVG, IR_AVG, AMBIENT_AVG;

//
// Pin Definitions.
//*6
#define MISO_PIN              19
#define MOSI_PIN              23
#define SCK_PIN               18
#define SS_PIN                5

#define VSPI_MISO             MISO
#define VSPI_MOSI             MOSI
#define VSPI_SCLK             SCK
#define VSPI_SS               SS_PIN
  
#define INT_PIN               17

#define GPIO1_PIN             16
#define GPIO2_PIN             4

#define RED                   12
#define IR                    14

//uninitalised pointers to SPI objects
MAX86141 pulseOx1;
//MAX86141 pulseOx2;

void setup() {
  Serial.begin(115200);

  //
  // Configure IO.
  //
  pinMode(SS_PIN, OUTPUT);
  pinMode(INT_PIN, INPUT_PULLUP);
  //pinMode(GPIO1_PIN, OUTPUT);
  //pinMode(GPIO2_PIN, INPUT_PULLUP);

  pinMode(RED, OUTPUT);
  pinMode(IR, OUTPUT);
  digitalWrite(RED, LOW);
  digitalWrite(IR, LOW);

  digitalWrite(SS_PIN, LOW);
  //digitalWrite(GPIO1_PIN, HIGH);

  //initialise SPI
  pulseOx1.spi = new SPIClass(VSPI);

  pulseOx1.SS = 5;
  //clock miso mosi ss

  //Serial.println("Init SPI Port...");
  //initialise vspi with default pins
  //SCLK = 18, MISO = 19, MOSI = 23, SS = 5, INT = 17
  Serial.println("Init Device");
  pulseOx1.spi->begin();
  delay(100);
  //Serial.println("Init Pulse Ox 1...");
  pulseOx1.setDebug(false);
  pulseOx1.init(spiClk);

  //Serial.println(pulseOx1.read_reg(0x0D));

  currentMicros = esp_timer_get_time();
  LEDMicros = currentMicros;

}

void switch_LED(){
  //pulseOx1.device_data_read();
  if(IR_ON){
      digitalWrite(RED,LOW);
      digitalWrite(IR,LOW);
      //Serial.println("AMBIENT");
      RED_ON = false;
      IR_ON = false;
      AMBIENT = true;
      return;
  }
  if(RED_ON){
    digitalWrite(RED,LOW);
    digitalWrite(IR,HIGH);
    //Serial.println("IR");
    RED_ON = false;
    AMBIENT = false;
    IR_ON = true;
    return;
  }
  if(AMBIENT){
    digitalWrite(IR,LOW);
    digitalWrite(RED,HIGH);
    //Serial.println("RED");
    AMBIENT = false;
    IR_ON = false;
    RED_ON = true;
    return;
  }
}

// the loop function runs over and over again until power down or reset
void loop() {
  
  currentMicros = esp_timer_get_time();
/*
  Serial.print("LED1");
  Serial.print(led1A);
  Serial.print("\t");
  Serial.println(led1B);

  Serial.print("LED2");
  Serial.print(led2A);
  Serial.print("\t");
  Serial.println(led2B);

  Serial.print("AMBIENT");
  Serial.print(pulseOx1.ambA[0]);
  Serial.print("\t");
  Serial.println(pulseOx1.ambB[0]);
*/

  //if(currentMicros - LEDMicros > LEDFrequency){  
    if(pulseOx1.read_reg(REG_FIFO_DATA_COUNT) >= 6){
      
      pulseOx1.device_data_read();
      int led1A = pulseOx1.led1A[0];
      int led2A = pulseOx1.led2A[0];
      int led1B = pulseOx1.led1B[0];
      int led2B = pulseOx1.led2B[0];

      /*
      float AVG = 0.16666666*(led1A + led1B + led2A + led2B + pulseOx1.ambA[0] + pulseOx1.ambB[0]);
      //Serial.println(AVG);
      if(RED_ON) RED_AVG = AVG;
      if(IR_ON) IR_AVG = AVG;
      if(AMBIENT) AMBIENT_AVG = AVG;

      if((IR_AVG != 0) && (RED_AVG != 0) && (AMBIENT_AVG != 0)){
        RED_AVG = RED_AVG - AMBIENT_AVG;
        IR_AVG = IR_AVG - AMBIENT_AVG;
        Serial.print("Red: ");
        Serial.print(RED_AVG);
        Serial.print("\t IR:");
        Serial.print(IR_AVG);
        Serial.print("\t Ratio: ");
        Serial.println(RED_AVG/IR_AVG);
        RED_AVG = 0;
        IR_AVG = 0;
        AMBIENT_AVG = 0;
      }
      */

      AMBIENT_AVG = (pulseOx1.led3A[0] + pulseOx1.led3B[0])*0.5;

      IR_AVG = (led2A + led2B)*0.5;
      Serial.print("\t");
      Serial.print("IR: ");
      Serial.print(IR_AVG);

      RED_AVG = (led1A + led1B)*0.5;
      Serial.print("Red: ");
      Serial.print(RED_AVG);

      Serial.print("\t");
      Serial.print("Ambient: ");
      Serial.println(AMBIENT_AVG); 

      float ratio = RED_AVG/IR_AVG;
      //Serial.print("\t");
      //Serial.print("Ratio: ");
      //Serial.println(ratio*4);
      
      //switch_LED();
      LEDMicros = currentMicros;
      //delayMicroseconds(2500);
      //pulseOx1.device_data_read();
    }
  //}
}

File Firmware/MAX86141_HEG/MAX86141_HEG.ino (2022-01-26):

//MAX86141 HEG Biofeedback Firmware. By Joshua Brewster - MIT License
//People who contributed: Diego Schmaedech, Michael Lyons, Ben Hale

#include "WiFi_API.h"
#include "BLE_API.h"


bool BLEtoggle = false;
bool toggleSleep = false;
bool WIFItoggle = false;
unsigned long bootMicros = 0;
unsigned long inputMicros;
uint8_t sleepTick = 0; //

/*
  Pins:
  SS:          P5
  SCLK:        P18
  MOSI:        P23
  MISO:        P19
  INT:         P17
  VLED1:       P22
  VLED2:       P21
  SWITCH OUT:  P13
  SWITCH BT:   P12
  SWITCH WIFI: P14
  SWITCH BLE:  P27 
  BTN IN:      P26
*/


void goToSleep() {
    EEPROM.write(510,0); //Disarm sleep toggle for next reset
    EEPROM.end();
    Serial.println("HEG going to sleep now... Reset the power to turn device back on!");
    delay(300);
    esp_deep_sleep_start(); //Ends the loop() until device is reset.
}



void toggleCheck(){ //Checks toggles on initialization
  while(currentMicros - bootMicros < 3500000){
    currentMicros = esp_timer_get_time();
    if((toggleSleep == false) && (currentMicros - bootMicros > 1000000)){
      EEPROM.begin(512);
      EEPROM.write(510,0); // Disarm the sleep toggle
      EEPROM.write(511,1); // Now arm the BLE/WiFi toggle
      EEPROM.end();
      toggleSleep = true;
      commandESP32('t');
      delay(100);
      commandESP32('f');
      Serial.println("Reset now to change the connection mode");
    }
    if((toggleSleep == true) && (BLEtoggle == false) && (currentMicros - bootMicros > 2000000) ){
      EEPROM.begin(512);
      EEPROM.write(511,0); //Disarm BLE/WiFi toggle
      EEPROM.write(509,1); // Now arm the Wifi reset toggle
      EEPROM.end();
      BLEtoggle = true;
      commandESP32('t');
      delay(100);
      commandESP32('f');
      Serial.println("Reset now to reset the WiFi credentials");
    }
    if((BLEtoggle == true) && (WIFItoggle == false) && (currentMicros - bootMicros > 3000000) ){
      EEPROM.begin(512);
      EEPROM.write(509,0); //Disarm BLE/WiFi toggle
      EEPROM.end();
      WIFItoggle = true;
      commandESP32('t');
      Serial.println("Running...");
    }
  }
}


void setup(){
  Serial.begin(115200);
  Serial.println();
  Serial.println("Booting...");

  currentMicros = esp_timer_get_time();
  pinMode(5,OUTPUT);
  
  EEPROM.begin(512);
  int sleep = EEPROM.read(510);
  if(sleep == 1){
    goToSleep();
  }
  int wifiReset = EEPROM.read(509);
  int toggle = EEPROM.read(511);
  int ComMode = EEPROM.read(0); //Communication mode (WiFi, BLE, or BT Serial)
  if(toggle == 1){
    if(ComMode == 1){
      ComMode = 0;
      EEPROM.write(0,0);
    }
    else if (ComMode == 0){
      ComMode = 2;
      EEPROM.write(0,2);
    } 
    else {
      ComMode = 1;
      EEPROM.write(0,1);
    }
  }
  //EEPROM.write(510,1); //Arm the sleep toggle (first in order of checks)
  //EEPROM.write(509,0); // Disarm the wifi login reset
  EEPROM.end();
  
  if(wifiReset == 1){
    saveWiFiLogin(true,false,false,false); //Reset WiFi credentials
  }

  setupHEG();

  commandESP32('f');

  pinMode(12, INPUT);  //Switch OUT
  pinMode(13, OUTPUT); //Switch BT
  pinMode(14, OUTPUT);  //Switch WIFI
  pinMode(27, OUTPUT);  //Switch BLE
  pinMode(26, INPUT);  //Button In

  Serial.println(ComMode);
  if(ComMode == 3) { 
    Serial.println("USB Only configuration.");
    Serial.println("Sample commands: 't': Toggle HEG program ON, 'f': Toggle HEG program OFF, 'u': Toggle WiFi mode, 'b': Toggle BLE mode, 'B': Toggle Bluetooth Serial mode");
  }
  digitalWrite(13, HIGH);
  delay(50);
  bool cset = false;
  if((digitalRead(12)) || ComMode == 2) { 
     setupBTSerial();
     commandESP32('t');
     delay(100);
     commandESP32('f');
     delay(100);
     commandESP32('t');
     delay(100);
     commandESP32('f');
     delay(100);
     commandESP32('t');
     delay(100);
     commandESP32('f');
     delay(100);
     commandESP32('t');
     delay(100);
     commandESP32('f');
     cset = true;
  } 
  digitalWrite(13,LOW);
  digitalWrite(14, HIGH);
  delay(50);
 if((digitalRead(12) && cset == false) || ComMode == 1) {
     setupWiFi();
     commandESP32('t');
     delay(100);
     commandESP32('f');
     delay(100);
     commandESP32('t');
     delay(100);
     commandESP32('f');
     delay(100);
     commandESP32('t');
     delay(100);
     commandESP32('f');
     cset = true;
  } 
  digitalWrite(14, LOW);
  digitalWrite(27, HIGH);
  delay(50);
 if(digitalRead(12) || cset == false) {
     setupBLE();
     commandESP32('t');
     delay(100);
     commandESP32('f');
     delay(100);
     commandESP32('t');
     delay(100);
     commandESP32('f');
     cset = true;
  }
  digitalWrite(27, LOW);
  //Now set up the communication protocols (Only 1 active at a time for best results!)
  bootMicros = esp_timer_get_time();
  //toggleCheck();
  commandESP32('t');
  Serial.println("Running...");
}



void checkInput()
{
  if (USE_BT == true)
  {
    while (SerialBT.available())
    {
      received = SerialBT.read();
      SerialBT.println(received);
      commandESP32(received); //Currently defined in WiFi_API.h due to some awkward coding
      SerialBT.read(); //Flush endline for single char response
    }
  }
  if (USE_USB == true)
  {
    while (Serial.available())
    {
      received = Serial.read();
      Serial.println(received);
      commandESP32(received);
      Serial.read();
    }
  }
}

void loop(){
  currentMicros = esp_timer_get_time();
  //Serial.print("Time (ms): ");
  //Serial.println(currentMillis);
  
  HEG_core_loop();
  if(newOutputFlag){
      outputSerial();
      outputBT();
      newOutputFlag = false;
  }
  if(currentMicros - inputMicros >= 330000){ // Check input every N microseconds
//    int SLP = digitalRead(26);
//    if(SLP == 1) {
//      sleepTick++;
//      if(sleepTick > 9) {
//        commandESP32('S');
//      }
//    } else { sleepTick = 0; }
    
    inputMicros = currentMicros;
    delayMicroseconds(1800);
    checkInput();
  }
}

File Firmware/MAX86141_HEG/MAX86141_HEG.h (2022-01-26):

#ifndef MAX86141_HEG_H
#define MAX86141_HEG_H
//MAX86141 HEG SCRIPT

#include "MAX86141.h"
#include "spo2_algorithm.h"
#include <CircularBuffer.h>
#include <esp_timer.h>
#include "IIRfilter.h"

bool USE_FILTERS = true;
bool USE_DC_FILTER = false;

float sps = 2048/3; //Samplerate per site: 

IIRnotch notch50_R(50,sps,0.5);
IIRnotch notch50_I(50,sps,0.5);
IIRnotch notch50_A(50,sps,0.5);

IIRnotch notch50_R2(50,sps,0.5);
IIRnotch notch50_I2(50,sps,0.5);
IIRnotch notch50_A2(50,sps,0.5);

IIRnotch notch50_R3(50,sps,0.5);
IIRnotch notch50_I3(50,sps,0.5);
IIRnotch notch50_A3(50,sps,0.5);

IIRnotch notch60_R(60,sps,0.5);
IIRnotch notch60_I(60,sps,0.5);
IIRnotch notch60_A(60,sps,0.5);

IIRnotch notch60_R2(60,sps,0.5);
IIRnotch notch60_I2(60,sps,0.5);
IIRnotch notch60_A2(60,sps,0.5);

IIRnotch notch60_R3(60,sps,0.5);
IIRnotch notch60_I3(60,sps,0.5);
IIRnotch notch60_A3(60,sps,0.5);

IIRlowpass lp_R(40,sps);
IIRlowpass lp_I(40,sps);
IIRlowpass lp_A(40,sps);

IIRlowpass lp_R2(40,sps);
IIRlowpass lp_I2(40,sps);
IIRlowpass lp_A2(40,sps);

IIRlowpass lp_R3(40,sps);
IIRlowpass lp_I3(40,sps);
IIRlowpass lp_A3(40,sps);

DCBlocker dc_R(0.995);
DCBlocker dc_I(0.995);
DCBlocker dc_A(0.995);

MAX86141 HEG1;
//MAX86141 HEG2;

static int spiClk = 1000000; // 8 MHz Maximum for MAX86141

bool USE_USB = true;

char outputarr[64];
bool newOutputFlag = false;
bool newEvent = false; //WiFi event task

bool RED_ON = false;
bool IR_ON = false;
bool AMBIENT = true;
char * MODE = "TEMP"; //SPO2, DEBUG, FAST, TEMP, EXT_LED (raw ambient mode with GPIO timer based external leds)
char * LEDPA = "FULL"; //FULL, HALF
char * EXPMODE = "DEFAULT"; //Exposure modes, DEFAULT, FAST, SLOW
char * LEDMODE = "DEFAULT"; //DEFAULT, 2IR, REDISAMB, 2IRAMB

bool coreProgramEnabled = false;

float RED_AVG, IR_AVG, AMBIENT_AVG, RATIO_AVG;
float v1, drdt, lastRatio;

//pulse Ox library variables
CircularBuffer<uint32_t, 200> redBuffer;
CircularBuffer<uint32_t, 200> irBuffer;
int32_t bufCap = 200;

int32_t spo2;
int8_t validSPO2;
int32_t lastValidSPO2;
int32_t heartRate;
int8_t validHeartRate;
int32_t lastValidHeartRate;
////

unsigned long currentMicros = 0;
unsigned long lastSampleMicros = 0;
unsigned long coreNotEnabledMicros = 0;
unsigned long lastSPO2Micros = 0;

unsigned long SPO2Freq = 25000; //SPO2/HR calculation frequency

bool DEEP_SLEEP_EN = true;
unsigned long sleepTimeout = 600000000; //10 minutes till sleep if no activity on sensor.

//Manual LED sampling controls.
unsigned long LEDMicros = 0;
unsigned long LEDFrequency = 7500; //Time (in Microseconds) between each change in LED state (Red, IR, Ambient);

//
// Pin Definitions.
//
#define MISO_PIN              19
#define MOSI_PIN              23
#define SCK_PIN               18
#define SS_PIN                5

#define VSPI_MISO             MISO
#define VSPI_MOSI             MOSI
#define VSPI_SCLK             SCK
#define VSPI_SS               SS_PIN

#define INT_PIN               17

#define GPIO1_PIN             16
#define GPIO2_PIN             4

#define RED                   12 //External LED gpio
#define IR                    14
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

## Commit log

2020-10-15 fixes in design I'm testing
    [MAX86141_HEG_MINI.brd]
2020-12-17 updated BOM
    [MAX86141HEG_BOM.xls]
2020-12-30 updates/another fix for boot routine
    [MAX86141HEG_BOM.xls, MAX86141_HEG_MINI.brd, MAX86141_HEG_MINI.sch, MAX86141_HEG_MINI_HEADPIECE.brd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]
2021-01-22 implement IIR filters (no more AC noise)
2021-01-23 BLE fix, filter tweak
2021-03-17 brighter red led
2021-04-24 minor fixes (reset and sleep command shuts sensor off correctly)
2021-04-27 added 'e' and 'l' commands to tweak exposure and LED settings.
2021-04-29 additional LED mode with 'l' to set red as ambient. Testing BLE OTA also
2021-05-09 enable die temp reading by default in last position
2021-06-07 uploaded dxf (will be updating boards soon however)
    [MAX86141_HEG_MINI.dxf, MAX86141_HEG_MINI_HEADPIECE.dxf]
2021-06-08 quality improvements to design (hopefully)
    [MAX86141_HEG_MINI.brd, MAX86141_HEG_MINI.sch, MAX86141_HEG_MINI_HEADPIECE.brd, MAX86141_HEG_MINI_HEADPIECE.sch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]
2021-06-17 headpiece update with switches
    [MAX86141_HEG_MINI_HEADPIECE.brd, MAX86141_HEG_MINI_HEADPIECE.dxf, MAX86141_HEG_MINI_HEADPIECE.sch, Stiffener_BOT.gbr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]
2021-06-20 more holes for switch mount
    [MAX86141_HEG_MINI.brd, MAX86141_HEG_MINI_HEADPIECE.brd, Stiffener_BOT.gbr, Stiffener_TOP.gbr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]
2021-07-08 reverted breakout board (trace spacing too narrow)
    [MAX86141HEG_BOM.xls, MAX86141_HEG_MINI.brd, MAX86141_HEG_MINI.sch, copper_bottom.gbr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]
2021-11-08 pushed firmware updates
    [MAX86141_HEG_MINI_HEADPIECE.brd, MAX86141_HEG_MINI_HEADPIECE.sch, Stiffener_BOT.gbr, Stiffener_TOP.gbr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]
2021-11-29 replaced update files, switch actually will work now (for newest boards with it installed)
2022-01-26 firmware tweaks + IR/Amb version (no Red LED by default)

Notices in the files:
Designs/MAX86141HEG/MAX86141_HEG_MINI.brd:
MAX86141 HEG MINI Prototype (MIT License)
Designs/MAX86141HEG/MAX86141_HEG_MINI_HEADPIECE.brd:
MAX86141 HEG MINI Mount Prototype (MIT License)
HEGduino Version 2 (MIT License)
